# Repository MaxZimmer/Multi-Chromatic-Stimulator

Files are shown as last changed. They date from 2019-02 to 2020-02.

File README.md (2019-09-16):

<p align="right">
<h1 align="center">Multi-Chromatic Stimulator</h1></p>
<h4 align="center">An OpenSource LED stimulator for visual and optogenetics stimulation in combination with 2-photon recording</h4>
<p align="center"><h6 align="right">by M.J.Y. Zimmermann, A.M. Chagas, P. Bartel, T. Baden</h6></p>

This project is licensed under the [GNU General Public License v3.0](https://github.com/MaxZimmer/Multi-Chromatic-Stimulator/blob/master/LICENSE)

The study of colour vision with fluorescence microscopy requires precise control over the spectra of visual stimuli.

Here we describe an effective, low-cost, opensource LED stimulator, designed to be used in combination with a 2-photon microscope. The design is built around an open-source development board and off-the-shelf components. It has been conceived to be assembled and used without the need for advanced electronics skills.

[Instruction Manual](https://github.com/MaxZimmer/Multi-Chromatic-Stimulator/tree/master/Manuscript%20and%20Instruction%20Manual)

***

## Repository structure

```
├───3D Designs                                Contains printed parts for the stimulator and optical components
│   ├───Optical Components
|   |   ├───STL renderings                    - Printing files
|   |   └───SCAD files                        - SCAD files to be modified if need be
│   └───Stimulator
|      ├───STL renderings                    - Printing files
|      └───SCAD files                        - SCAD files to be modified if need be
|
├───Arduino Code                              Stimulator Code
|   ├───Stimulator Code                       - Adaptable C+ code for running the stimulator
|   └───LED driver library                     - Library to run the TLC 5947
|
├───Bill of Materials                         List of necessary components and retailer suggestions
|
├───Datasheets                                - Contains all technical sheet for:
|   ├───Optical Components                    - ...LEDs, Filters, Dichroic Mirrors used in the presented example
|   ├───Stimulator                            - ...micro-controller and LED driver
|   └───Spectrometer                          - ...device used for calibration
|
├───Images                                    Image repository
|
├───Instruction Manual                        Detailed manual to assemble and calibrate the stimulator
|   └───Stimulator Calibration                - Contains calibration recordings and the adaptable jupyter notebook script to calibrate the stimulator
|       ├───Arduino Calibration Code          - Sequence used for the calibration
|       ├───Filters                           - Filters and dicroic mirrors spectra
|       ├───Powermeter Recording              - Recording of the calibration sequence
|       └───Spectrometer Recording            - Recording of the calibration sequence
|
├───PCB                                       KiCad and Gerber files to modified and generate PCB for:
│   ├───Potentiometer mounts                  - ...trimmer potentiometers that set the LED maximum brightness
│   └───Stimulator                            - ...the stimulator itself
|
└───References                                Publication used to design and conceive this model

```

***

The following design can control up to 24 spectral channels with 12 bits linear resolution and 25 μs temporal precision. Our system only requires simple electronics components to be assemble and can be combined.
Built around an ESP32 micro-controller an LED driver (Adafruit model) and off-the-shelf components for a total cost of ~$50

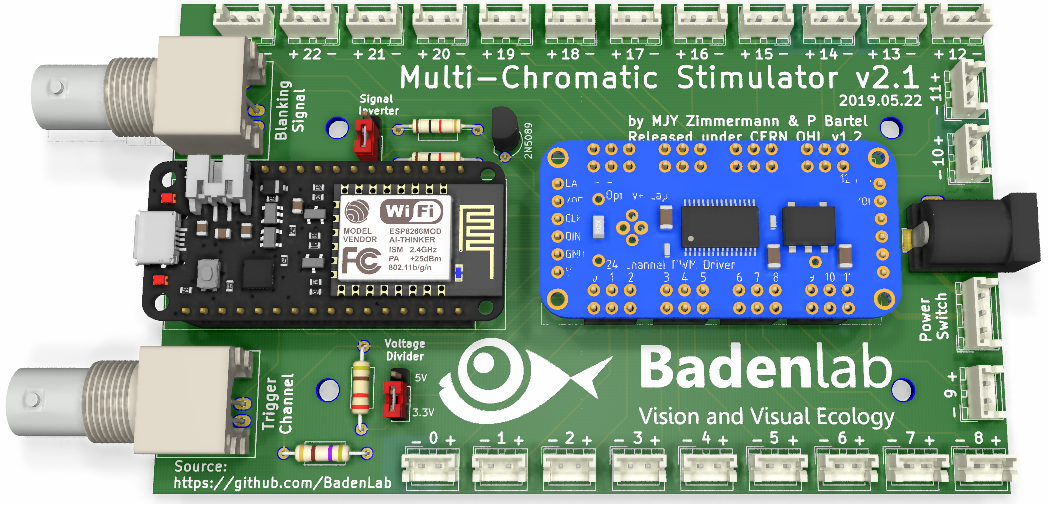
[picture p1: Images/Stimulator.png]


***

The stimulator runs synchronous to the recording system using TTL triggers.
TTL signals correspond to scanning mirror retrace periods and are used to turn ON and OFF LEDs, thus avoiding swamping the PMTs by stimulation light.

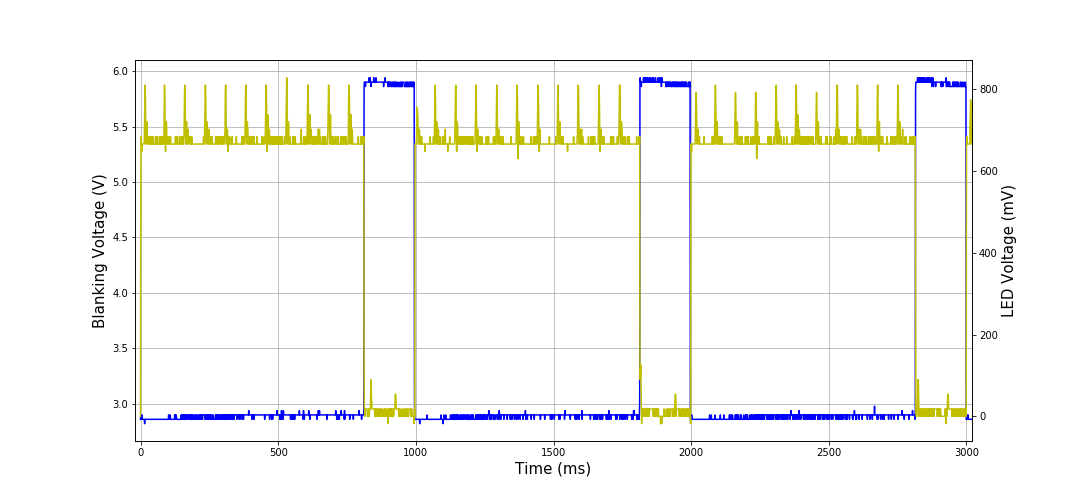
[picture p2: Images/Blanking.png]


***

The following design was adjusted for the tetrachromatic zebrafish.
Stimulating LEDs and optical filters were chosen to match the peak sensitivities of opsin spectra while avoiding overlap with the PMT detection bands.

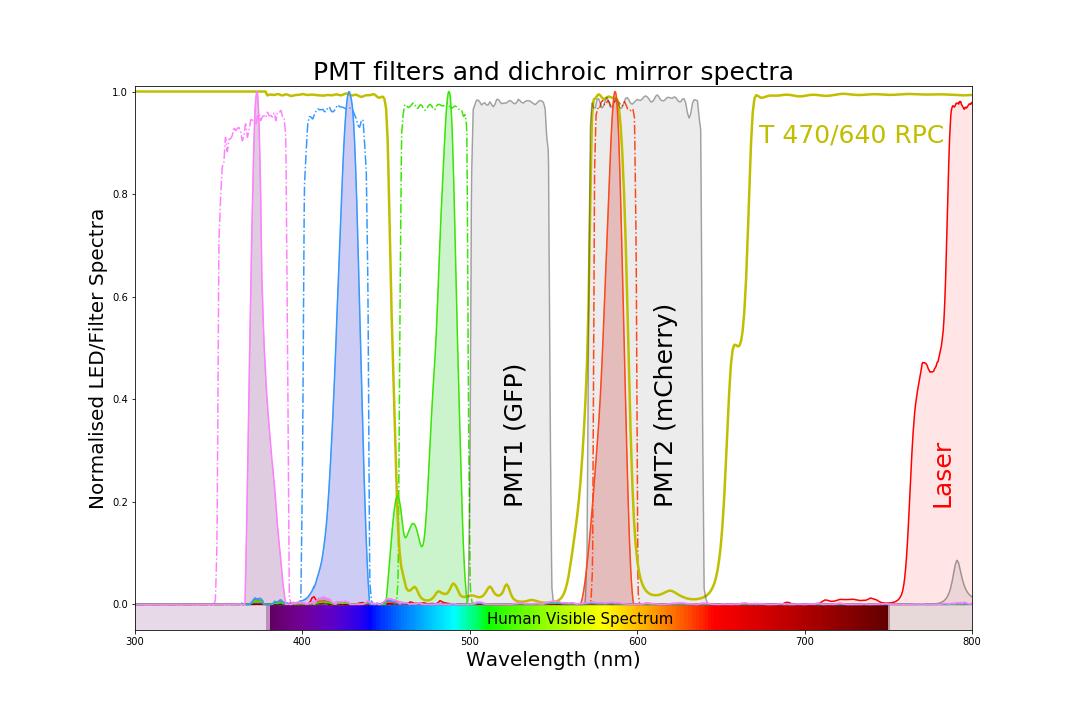
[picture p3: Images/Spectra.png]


***

In this example, light sources are combined and directed through the onjective.

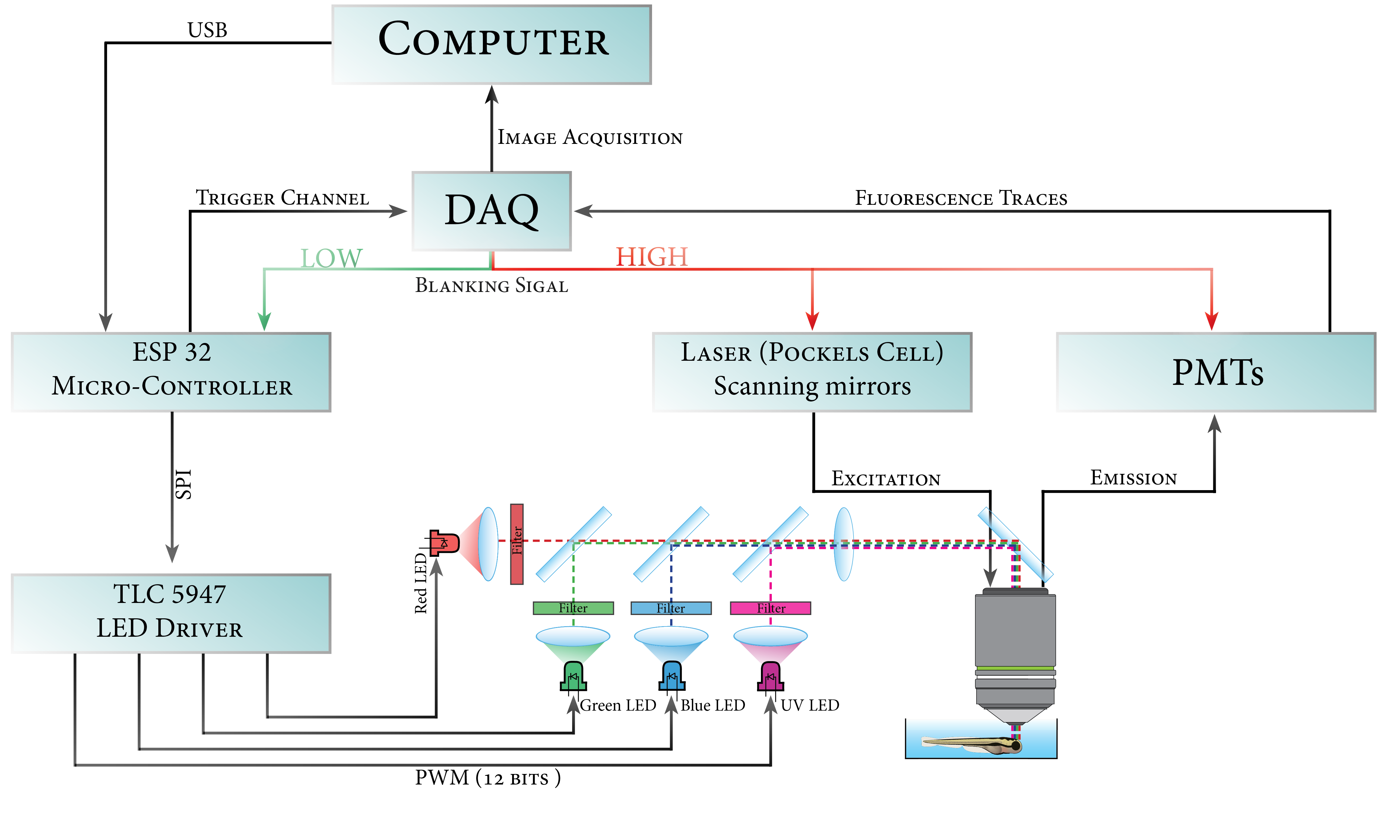
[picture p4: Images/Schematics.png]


***

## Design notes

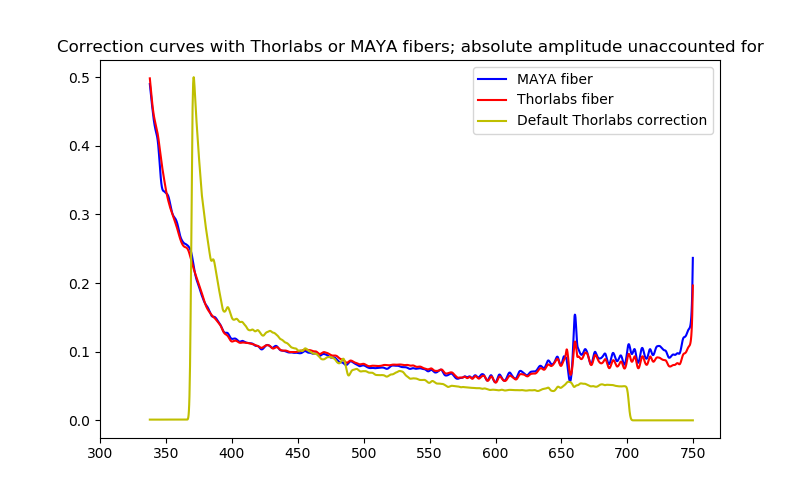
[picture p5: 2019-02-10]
Instruction Manual/Stimulator Calibration/Spectrometer_Recording/Spectrometer Correction Curves/Correction_curves.png

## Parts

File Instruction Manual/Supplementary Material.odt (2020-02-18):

Supplementary Material

Overview

This document contains detailed assembly instructions, a software guideline to customize stimuli, and includes a parts list. The Arduino code and 3D printing files (SCAD and STL) can be downloaded at https://github.com/BadenLab/Tetra-Chromatic-Stimulator/ and further modified to fit customise purposes. The aim of this device is to finely control LEDs used in combination with a 2-photon microscope.

The device consists of a custom-designed PCB, an ESP32 development board (or an Arduino Nano if the stimulator does not need to be combined with a 2-photon microscope), an LED driver and various off-the-shelf components. (Fig. S1).

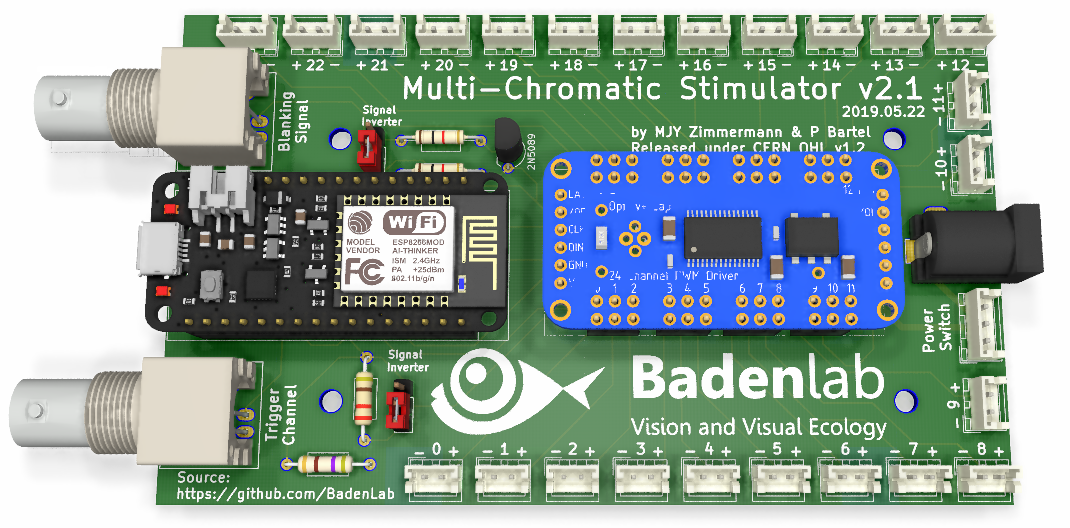
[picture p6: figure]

Figure S1

Bill of Materials

Name | Manufacturer | Order ID | Retailer | Quantity | Observation 1 | Observation 2 | Cost
Adafruit Huzzah32 - ESP32 Feather | Adafruit | 3405 | Adafruit | 1 | Development Board | | £17
Adafruit TLC5947 | Adafruit | 1429 | Adafruit | 1 | LED Driver | | £12
BNC coaxial connectors | TE Connectivity | 1-1337542-0 | Farnell | 2 | Electronics | Right angle jacks, 50ohm | £3.70
2 way JST Female Connector Housing | RS Online | 820-1611 | JST | 8 | Electronics | | £3.80
3 way JST Female Connector Housing | RS Online | 820-1614 | JST | 1 | Electronics | | £1.90
4 way JST Female Connector Housing | RS Online | 820-1618 | JST | 2 | Electronics | | £1.90
2 way JST PCB header | RS Online | 820-1554 | JST | 8 | Electronics | | £3.80
3 way JST PCB header | RS Online | 820-1557 | JST | 1 | Electronics | | £1.90
4 way JST PCB header | RS Online | 820-1551 | JST | 2 | Electronics | | £1.90
JST Crimp Connector Wire | RS Online | 820-1548 | RS | 15 | Electronics | | £10.00
3 mm LED | Digikey | 350-1557-ND | Digikey | 4 | Electronics | 3mm round, Through hole | £2
Mount for 3 mm LED | Digikey | 67-1330-ND | Digikey | 4 | Electronics | 3mm panel mount | £1
Mount for 5 mm LED | Digikey | 67-1332-ND | Digikey | 4 | Electronics | 5mm panel mount | £1
Rocker LED switch | | | Ebay | 1 | Electronics | Round Switch / 3 pins | £2.50
220 Ohms Resistor | RS Online | 707-7612 | RS | 1 | Electronics | Through hole | £1.16
470 Ohms Resistor | RS Online | 707-7647 | RS | 1 | Electronics | Through hole | £1.16
10 kOhms Trimmer Potentiometer | TT Electronics | 89PR10KLF | Farnell | 4 | Electronics | Through Hole | £5.95
PCB socket | Samtec | SSW-116-02-G-S | RS | 6 | Electronics | 1 row, 15 pin | £3
2.1 mm right angle DC socket | RS Online | 884-0957 | RS | 1 | Electronics | 2.1 mm right angle | £1
Solderable Breadboard | Roth Elektronik | RE944-S1 | RS | 1 | Electronics | 42.54 x 31.75 | £1.76
Distinct colour wires | RS Online | 331-862 | RS | 100 cm | Electronics | 20 AWG | £5
Cable shrink | RS Online | 170-6377 | RS | 20 cm | Electronics | Shrunk diameter 1.2 mm | £1.58
M3 x 10mm screw | RS Online | 660-4636 | RS | 4 | Mechanical | M3 x 10 Hex socket cap | £4
M3 nut | RS Online | 122-4400 | RS | 4 | Mechanical | M3 nuts | £4
M4 x 50mm Hex Socket Cap Screws | RS Online | 304-4592 | RS | 4 | Mechanical | M4 x 50 | £4
M4 nut | RS Online | 189-579 | RS | 4 | Mechanical | M4 nuts | £4
| | | | | | | £101

Assembling the Stimulator

1 – Obtaining the custom-designed PCB

From the GitHub repository (https://github.com/BadenLab/Tetra-Chromatic-Stimulator/tree/master/PCB/Stimulator), one can find the gerber.zip folder needed to order the PCB to any manufacturer company (i.e. https://jlcpcb.com). Ordering a minimum of five units should not cost more than £10. Gerber files were designed with KiCad 5.0. Schematics and PCB footprint can be downloaded and modified from the same repository if need be (Fig. S2).

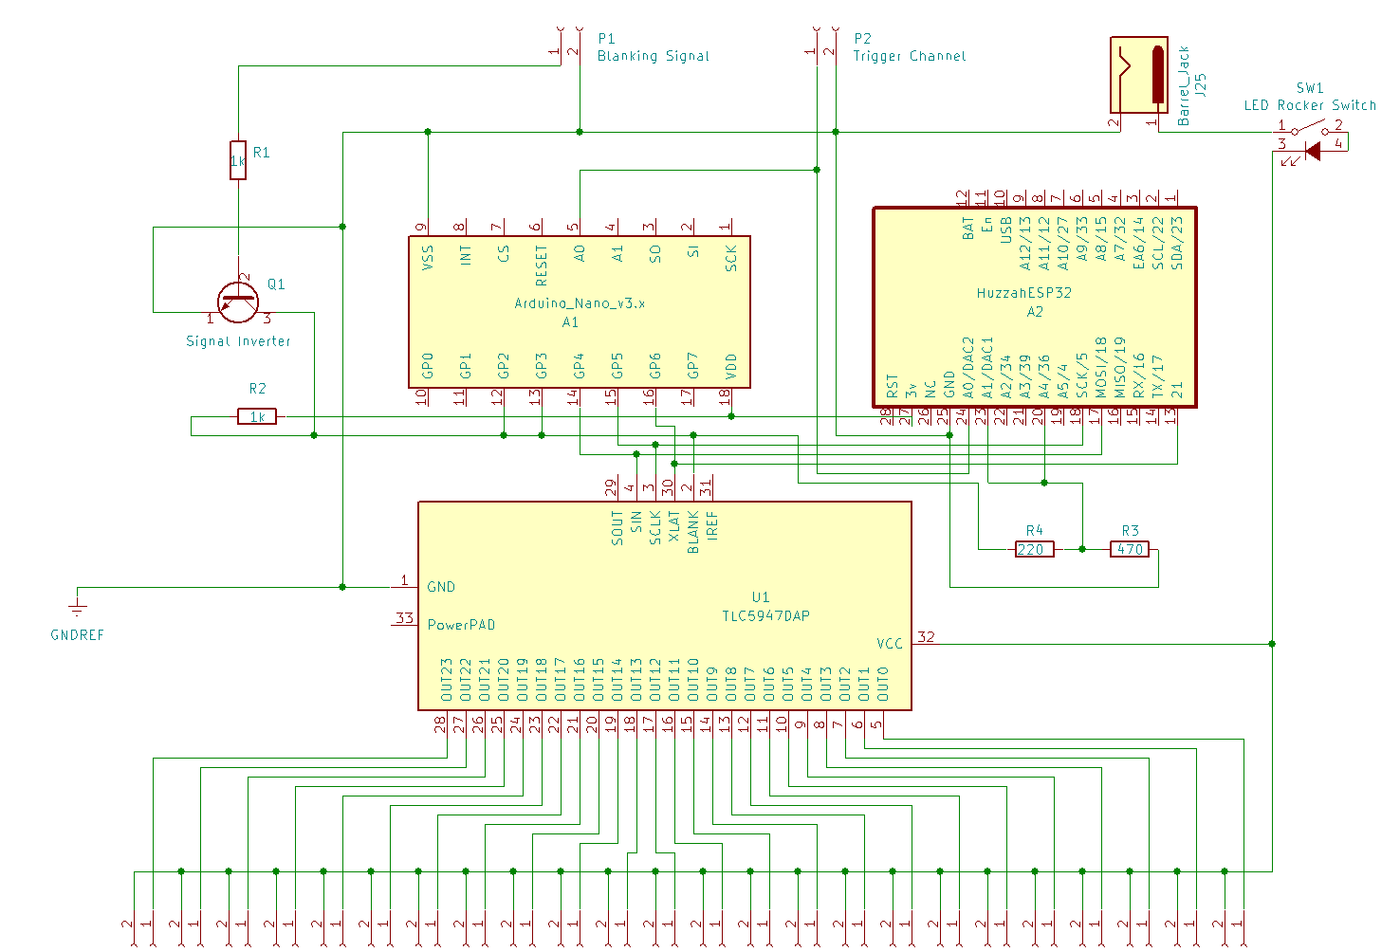
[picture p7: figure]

Supplementary Figure S2.

2 – Soldering the custom-designed PCB

The board is self-explanatory. On the left, two options are available, one for the Arduino (close rows) the other for the ESP (spread rows). There is no need to solder more JST pins that the number of LED required for the desired stimulator (here 8 JST pin are connected: 4 for the stimuli LEDs, 4 for their proxy LEDs).

The jumper on the top (Signal Inverter) allows the inversion of the TTL "Blanking" signals. For ScanImage users, the jumper should be placed at the upper position.

The jumper at the bottom of the board (Voltage Divider) allows to tune down the voltage from 5 to 3.3V if the ESP is used instead of an Arduino. ESP32 unlike Arduino Nano, works on a 3.3V logic; no higher tension should be sent to this board. Since most TTL deliver 5V pulses, we selected a 220/470Ω divider to bring a 5V blanking signal into a 3.3V input. Depending on the blanking signal generator used, this divider can be modified to fit one’s personal design or bypassed by only bridging the 220Ω resistor.

The Adafruit TLC5947 LED driver is a constant current driver configured by default to set the current level at 15mA per channel, which is virtually safe for any LED. However, one can operate at different current by replacing the on-board reference resistor with a through hole resistor. The driver is capable to deliver up to 30mA, the graph in FIG S4 shows the relationship between resistance and output current.

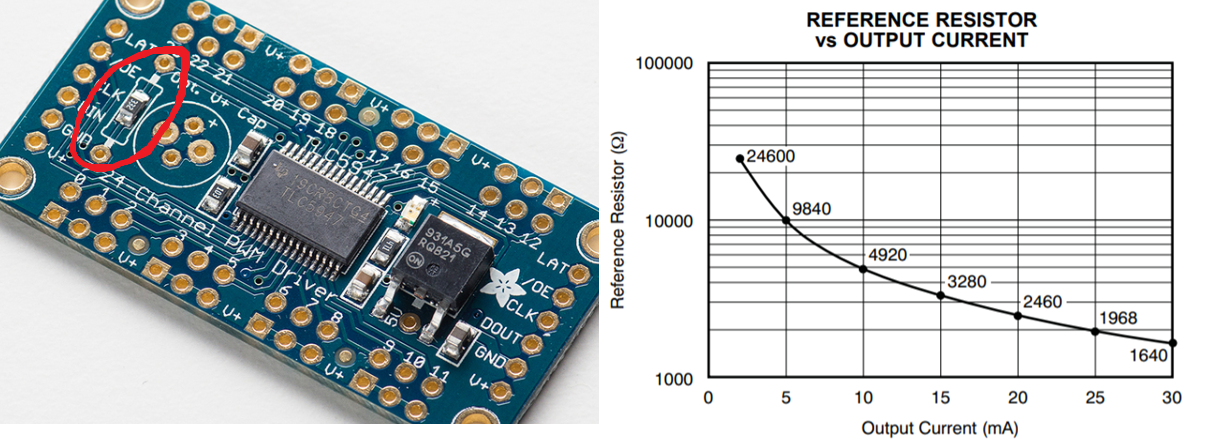
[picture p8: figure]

Supplementary Figure S4

3 – Mounting the potentiometer

In order to finely adjust each LED power, we added multiple-turn trimmer potentiometers to our design. A simple solution is to manufacture the appropriate PCB board (We provide multiple options on the GitHub repository).

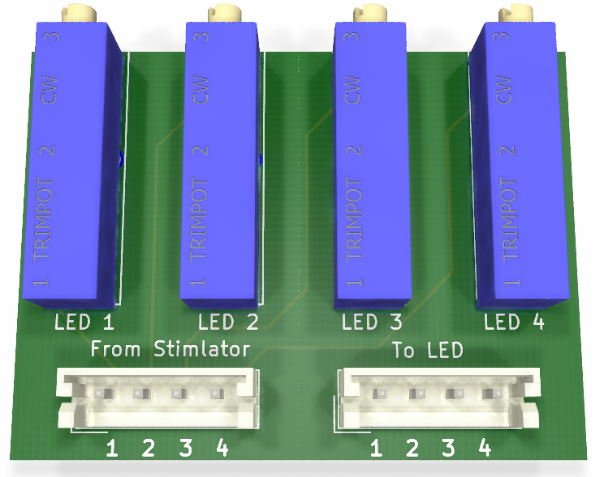
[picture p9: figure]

Otherwise, one can make its own little PCB by using a solderable board. Each potentiometer connects its ClockWise (pin 3) to the LED (+) stimulator JST pin; and its Base (pin 2) to the LED (+) leg. The LED (-) stimulator JST pin connects the LED (-) leg directly.

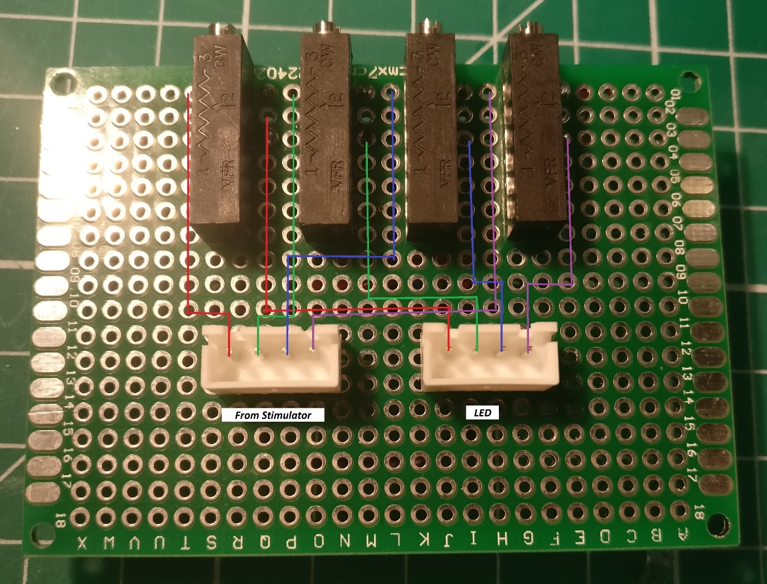
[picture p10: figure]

4 – Printing the Stimulator box

STL files can be found on the GitHub repository and print directly if the user wishes to go for the default design (4 stimulation LEDs + 4 proxy LEDs) and BoM. However, SCAD files are also available and easily adjustable for personalised design (Fig. S6).

We used OpenSCAD (freely available at www.openscad.com) to design the stimulator box. The tolerance of the printer can be adjusted in the “USER Parameters” section of the script (tol =0.1; by default, this value is used for Prusa MK3 and Ultimaker 2). Each component can be displayed/design individually in the “Switches” section. Variables such as LED number (4 by default) and the potentiometer board dimensions can be adjusted in the “Component Parameters” section.

The PCB is screwed to the “Bottom” part of the box by using M3 screws and nuts. The potentiometer board adjusts itself with the “Back” part of the box, and the trimmers should adapt to their respective holes exactly.

All part should fit tightly together and are maintained together by 4 M3*50mm socket screws.

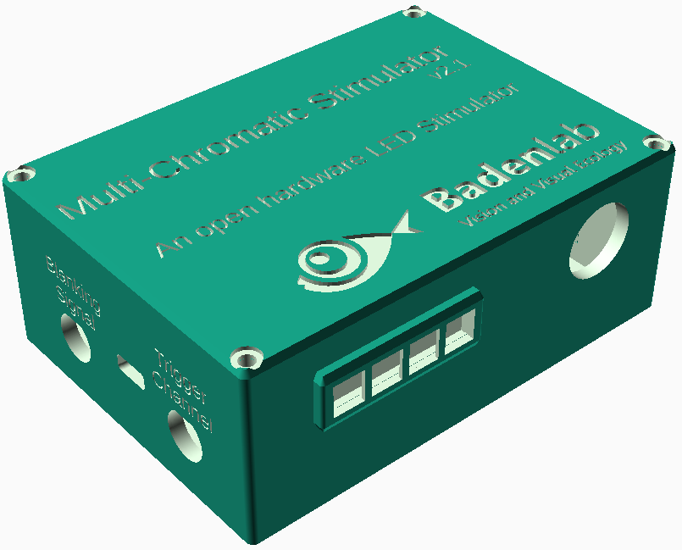
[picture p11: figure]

5 – Adjusting the proxy LED

The proxy LED are markers for the experimenters to have a ready visualisation of the stimulus being displayed under the objective. If this option is selected, 3mm LED are to be mounted at the back of the LED holder using 3mm LED mount. Finally, any translucid material could be placed in the LED holder slot in order to diffuse the proxy LED light (In our example, we used a piece of thin Teflon)

6 – Connecting the Stimulator

The stimulator can be powered from 5 to 30v. The Adafruit TLC5947 being a constant current LED driver, the voltage selection is not critical, however it has to be slightly higher than the LED forward voltage (LED datasheet). Multiple LEDs can be connected to the same channel; however, the voltage supply has to be adjusted in consequence. For example, if an LED has 3.2v forward voltage, then a power supply => 3.2v will be enough, however if 5 of those LEDs are connected in series to the same channel, then the power supply has to be => 3.2v * 5 => 16v.

Blanking signal BNC has to be connected to a TTL (pulse generator), that delivers 5V pulses (if voltage is different, refer yourself to the soldering paragraph). Here we called blanking signal the pulse synchronised with the scanning mirror, the laser pocket cell and the PMTs. On our setup, when blanking signal is HIGH, the scanning mirror starts a new scanning line, the pocket cell let the laser beam through, the PMT records the emitting fluorescence and the stimulating LEDs are turned off. When the blanking signal is LOW, the opposite occurs.

The trigger channel is an output signal generated by the stimulator that by default sends a 3.3v pulse (if ESP32 is used, 5v for Arduino nano) at the start of the stimulus and then at every 1.00000s. This trigger is used during the analysis to correlate the displayed stimulus to the fluorescence trace recordings.

Finally, the board is connected to a computer via micro USB cable (for ESP32, mini USB for Arduino Nano), and ready to be used.

Programming the ESP32 (or Arduino)

1. Download and install Arduino environment on the computer (www.arduino.org).
2. To use the ESP32, a couple of steps are necessary
  a. Install the latest SiLabs CP2104 driver (https://www.silabs.com/products/development-tools/software/usb-to-uart-bridge-vcp-drivers).
  b. Follow the installation instructions from the Espressif repository (https://github.com/espressif/arduino-esp32/blob/master/docs/arduino-ide/boards_manager.md).
3. Install the TLC5947 library
  c. Start Arduino and from the “Sketch” tab, select “Include Library” and open “ Manage Libraries”
  d. From the search bar enter “TLC5947”
  e. Select and Install the library
4. Close Arduino and open the Multi-Chromatic-Stimulator arduino file from the “Arduino Code” folder.
5. From the “Tools” tab:
  f. For the ESP32:
    i. Select from “Boards” the “Adafruit ESP32 Feather”
    ii. From “Upload Speed”, select 921600
    iii. From “Flash Frequency”, select 80Hz
    iv. From “Port”, select the computer port to which the ESP is connected (if doubt, unplug, replug and observe the choices differences). If the ESP is not recognised, check the driver installation (2a.), then check the micro USB cable.
  g. For the Arduino Nano
    v. Select from “Boards” the “Arduino Nano”
    vi. From “Processor”, select “ATmega328P” (option Old Bootloader for clones or older arduino versions)
    vii. From “Port”, select the computer port to which the Arduino is connected (if doubt, unplug, replug and observe the choices differences). If an Arduino clone is used, check that the proper driver is installed on the computer (Board datasheet) then check the mini USB cable.
6. Compile and Upload the code by clicking on the arrow button on the top left.
7. The stimulator is ready to be used.

Operating the Stimulator

The code is organised in five distinct part:

Stimulus Parameters

Here, the user determines the sequence of his looping stimulus.

- The array_LED# corresponds to the sequence of each LED#. The value corresponds to the LED power and CAN ONLY TAKE A VALUE FROM 0 TO 100, where 0 corresponds to no light and 100 to max light intensity
- The array_Time corresponds to the duration of each entry in ms; the first entry being the pre-adaptation that will only be played at the start of the stimulus, the sequence will then loop starting at the second position.
- The number of Loops is determined by nLoops. The stimulus will stop after finishing the n Loop.
- IMPORTANT, for the code to work flawlessly, the number of entries within the arrays has to be the same and manually entered in nArrayEntries (including the pre-adaptation at position 1).

Microcontroller Board Selection

This is where the user defines if he is using an ESP32 or an Arduino Nano

Internal Definitions

This is the main definition part of the code which can be modified to:

- Add more LEDs than the 4 main and 4 proxy defined by default. (Global variables, the LED pins correspond to the pin number on the TLC5947).
- Adjust the trigger duration (25ms by default).
- Adjust the Trigger interval (1000 ms by default)

Internal Methods

This is the main core of the code and should not be structurally changed apart from adding more LEDs (straight forward)

Main Loop

This is where the stimuli controls are defined. By default, when compile window is open (magnifying glass on the top right corner) and the baud rate at the bottom right of the window has be changed to 115200, a manual command will trigger a stimulus:

By default:

- a – Play stimulus at max power
- b – Play stimulus at min power
- 0 – Turn off all LEDs stop any stimulus being played and reset the loop
- + – Turn on all LED to max power
- - – Turn on all LED to min power
- 1 – Turn First LED to max power
- 2 – Turn First LED to min power
- 3 – Turn Second LED to min power
- 4 – Turn Second LED to min power
- 5 – Turn Third LED to min power
- 6 – Turn Third LED to min power
- 7 – Turn Fourth LED to min power
- 8 – Turn Fourth LED to min power

Important to note, obviously the stimulation will only be played if a blanking signal is sent to the board.

Calibrating the stimulator

The TLC5947 is 12 bits PWM grayscale driver, meaning that it offers a 4096 degree of freedom to adjust each LED power.

On the arduino code there is a second tab called “LED_values” which hard-codes the maximum power an LED can get. Those values range from 0 (no current) to 4095 (max current, 15mA by default).

On the default script we proposed two distinct max values (oddly named here max and min power) that can be called individually. The purpose here is to have the opportunity to use the same stimulus sequence at two different light intensities. Off course more can be added manually by the user.

For the calibration, we suggest setting the max_LED# value at 4095 (Full power) and use successively a spectrometer and a powermeter. To adjust the LED brightness, the user should first use the trimmer potentiometer at the back of the stimulator then finely tune the desired max power in the code. When the LED value (0-100) will be entered in the stimulus sequence, it will automatically be mapped to 0-max_LED#

In this document we will used, as example, the visual stimulator built for the chromatic visual study of one of our animal models: the larval zebrafish. As this model possesses four cones photoreceptors that can be categorized as Red-, Green-, Blue- and UV-sensitive we designed a custom-built tetrachromatic stimulator with four LEDs that matches the peak sensitivity of those photoreceptors.

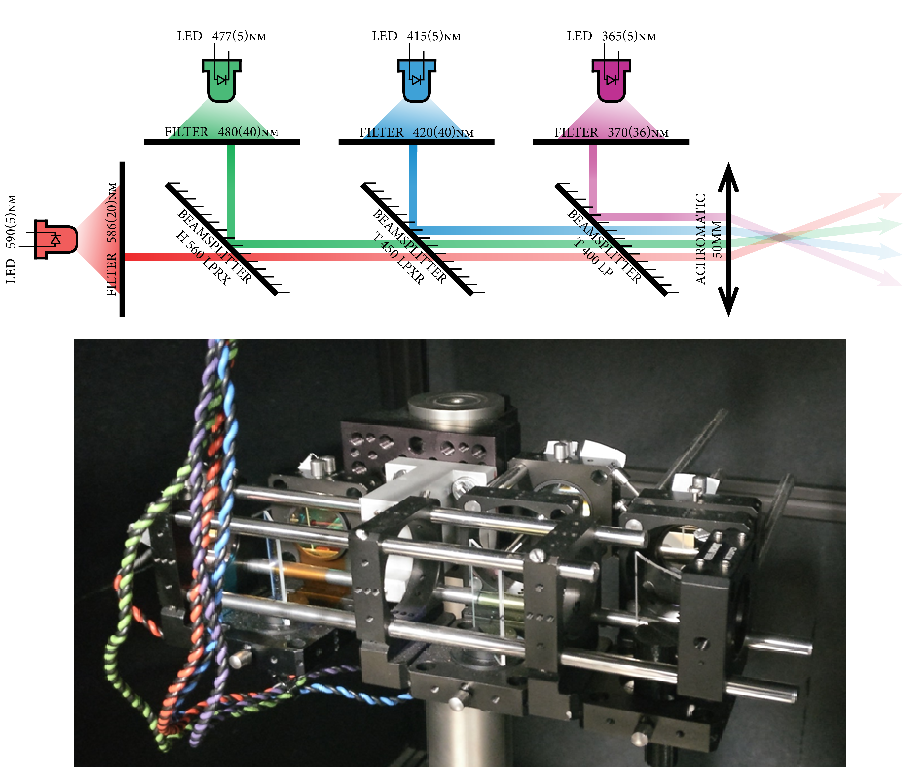
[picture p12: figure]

Optogenetics Stimulator

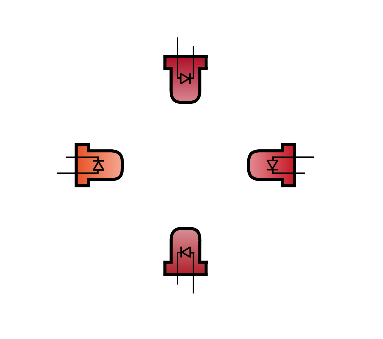
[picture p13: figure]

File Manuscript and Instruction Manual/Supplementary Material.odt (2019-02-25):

Supplementary Material

MultiChromatic Stimulator (need a proper name): an opensource LED stimulator for visual and optogenetics stimulation in combination with 2-photon recording

M.J.Y. Zimmermann, A.M. Chagas, P. Bartel, T. Baden

Affiliations:

1. School of Life Sciences, University of Sussex, United Kingdom
2. Institute for Ophthalmic Research, University of Tuebingen, Germany
3. TReND in Africa gUG (www.TReNDinAfrica.org)

Correspondence: T.B.: t.baden@sussex.ac.uk

Need illustration picture

Name | Manufacturer | Order ID | Retailer | Quantity | Observation 1 | Observation 2 | Cost
Adafruit Huzzah32 - ESP32 Feather | Adafruit | 3405 | Adafruit | 1 | Development Board | Easier to order it with header pins soldered | £17
Adafruit TLC5947 | Adafruit | 1429 | Adafruit | 1 | LED Driver | | £12
BNC coaxial connectors | TE Connectivity | 1-1337542-0 | Farnell | 2 | Electronics | Right angle jacks, 50ohm | £3.70
2 way JST Female Connector Housing | RS Online | 820-1611 | JST | 8 | Electronics | | £3.80
3 way JST Female Connector Housing | RS Online | 820-1614 | JST | 1 | Electronics | | £1.90
4 way JST Female Connector Housing | RS Online | 820-1618 | JST | 2 | Electronics | | £1.90
2 way JST PCB header | RS Online | 820-1554 | JST | 8 | Electronics | | £3.80
3 way JST PCB header | RS Online | 820-1557 | JST | 1 | Electronics | | £1.90
4 way JST PCB header | RS Online | 820-1551 | JST | 2 | Electronics | | £1.90
JST Crimp Connector Wire | RS Online | 01SHXSXH-26L 150 | RS | 15 | Electronics | | £10.00
3 mm LED | Digikey | 350-1557-ND | Digikey | 4 | Electronics | 3mm round, tht | £2
Mount for 3 mm LED | Digikey | 67-1330-ND | Digikey | 4 | Electronics | 3mm panel mount | £1
Mount for 5 mm LED | Digikey | 67-1332-ND | Digikey | 4 | Electronics | 5mm panel mount | £1
Rocker LED switch | | | Ebay | 1 | Electronics | Round Switch / 3 pins | £2.50
220 Ohms Resistor | RS Online | 707-7612 | RS | 1 | Electronics | Through hole | £1.16
470 Ohms Resistor | RS Online | 707-7647 | RS | 1 | Electronics | Through hole | £1.16
10 kOhms Trimmer Potentiometer | TT Electronics | 89PR10KLF | Farnell | 4 | Electronics | Through Hole | £5.95
PCB socket | Samtec | SSW-116-02-G-S | RS | 6 | Electronics | 1 row, 15 pin | £3
2.1 mm right angle DC socket | RS Online | 884-0957 | RS | 1 | Electronics | 2.1 mm right angle | £1
Solderable Breadboard | Roth Elektronik | RE944-S1 | RS | 1 | Electronics | 42.54 x 31.75 | £1.76
distinc colour wires | RS Online | 331-862 | RS | 100 cm | Electronics | 20 AWG | £5
Cable shrink | RS Online | 170-6377 | RS | 20 cm | Electronics | Shrunk diameter 1.2 mm | £1.58
M3 x 10mm screw | RS Online | 660-4636 | RS | 4 | Mechanical | M3 x 10 Hex socket cap | £4
M3 nut | RS Online | 122-4400 | RS | 4 | Mechanical | M3 nuts | £4
M4 x 50mm Hex Socket Cap Screws | RS Online | 304-4592 | RS | 4 | Mechanical | M4 x 50 | £4
M4 nut | RS Online | 189-579 | RS | 4 | Mechanical | M4 nuts | £4
| | | | | | | £101

Overview

This document contains detailed assembly instructions, a software guideline to customize stimuli, and includes a parts list. The Arduino code and 3D printing files (SCAD and STL) can be downloaded at https://github.com/BadenLab/Stimulator????, and further modified to fit customise purposes. The aim of this device is to finely control LEDs used in combination with a 2-photon microscope.

The device consists of a custom-designed PCB, a ESP32 development board (or an Arduino Nano if the stimulator does not need to be combined with a 2 photon microscope), a LED driver and various off-the-shelf components. (Fig. S1).


Supplementary Figure S1

Assembling the Stimulator

1 – Obtaining the custom-designed PCB

From the GitHub repository (https://github.com/BadenLab/?????/PCB), one can find the gerber.zip folder needed to order the PCB to any manufacturer company (i.e. https://jlcpcb.com). Ordering a minimum of 5 units should not cost more than £10. Gerber files were designed with KiCad 5.0. Schematics and PCB footprint can be downloaded and modified from the same repository if need be (Fig. S2).


Supplementary Figure S2.

2 – Soldering the custom-designed PCB

The board is self-explanatory (Fig. S3). On the left, two options are available, one for the Arduino (close rows) the other for the ESP (spread rows). There is no need to solder more JST pins that the number of LED required for the desired stimulator (here 8 JST pin are connected: 4 for the stimuli LEDs, 4 for their proxy LEDs). The two resistors at the bottom are a voltage divider for the ESP32 only (There’s no need to solder any resistor here if the Arduino option is chosen). ESP32 unlike Arduino Nano, works on a 3.3V logic; no higher tension should be sent to this board. Since most TTL deliver 5V pulses, we selected a 220/470Ω divider to bring a 5V blanking signal into a 3.3V input. Depending on the blanking signal generator used, this divider can be modified to fit one’s personal design or bypassed by only bridging the 220Ω resistor.

Supplementary Figure S3 TESSA PICTURE

The Adafruit TLC5947 LED driver is a constant current driver configured by default to set the current level at 15mA per channel, which is virtually safe for any LED. However, one can operate at different current by replacing the on-board reference resistor with a through hole resistor. The driver is capable to deliver up to 30mA, the graph in FIG S4 shows the relationship between resistance and output current.


Supplementary Figure S4

3 – Mounting the potentiometer

In order to finely adjust each LED power, we added multiple-turn trimmer potentiometers to our design. A simple solution is to manufacture the appropriate PCB board (We provide multiple option on the GitHub repository). Otherwise, one can make its own little PCB by using a solderable board and connect the potentiometer as shown on FIG S5.

Each potentiometer connects its ClockWise (pin 3) to the LED (+) stimulator JST pin; and its Base (pin 2) to the LED (+) leg. The LED (-) stimulator JST pin connects the LED (-) leg directly.


Supplementary Figure S5

4 – Printing the Stimulator box

STL files can be found on the GitHub repository and print directly if the user wishes to go for the default design (4 stimulation LEDs + 4 proxy LEDs) and BoM. However, SCAD files are also available and easily adjustable for personalised design (Fig. S6).

We used OpenSCAD (freely available at www.openscad.com) to design the stimulator box. The tolerance of the printer can be adjusted in the “USER Parameters” section of the script (tol =0.1; by default, this value is used for Prusa MK3 and Ultimaker 2). Each component can be displayed/design individually in the “Switches” section. Variables such as LED number (4 by default) and the potentiometer board dimensions can be adjusted in the “Component Parameters” section.

The PCB is screwed to the “Bottom” part of the box by using M3 screws and nuts. The potentiometer board adjusts itself with the “Back” part of the box, and the trimmers should adapt to their respective holes exactly.

All part should fit tightly together and are maintained together by 4 M3*50mm socket screws.


Supplementary Figure S6

5 – Adjusting the proxy LED

The proxy LED are markers for the experimenters to have a ready visualisation of the stimulus being displayed under the objective. If this option is selected, 3mm LED are to be mounted at the back of the LED holder using 3mm LED mount (Fig S7). Finally, any translucid material could be placed in the LED holder slot in order to diffuse the proxy LED light (In our example, we used a piece of thin Teflon)

TESSA PICTURE OF THE LED HOLDER Supplementary Figure S7

6 – Connecting the Stimulator

The stimulator can be powered from 5 to 30v. The Adafruit TLC5947 being a constant current LED driver, the voltage selection is not critical, however it has to be slightly higher than the LED forward voltage (LED datasheet). Multiple LEDs can be connected to the same channel; however, the voltage supply has to be adjusted in consequence. For example, if an LED has 3.2v forward voltage, then a power supply => 3.2v will be enough, however if 5 of those LEDs are connected in series to the same channel, then the power supply has to be => 3.2v * 5 => 16v.

Blanking signal BNC has to be connected to a TTL (pulse generator), that delivers 5V pulses (if voltage is different, refer yourself to the soldering paragraph). Here we called blanking signal the pulse synchronised with the scanning mirror, the laser pocket cell and the PMTs. On our setup, when blanking signal is HIGH, the scanning mirror starts a new scanning line, the pocket cell let the laser beam through, the PMT records the emitting fluorescence and the stimulating LEDs are turned off. When the blanking signal is LOW, the opposite occurs.

The trigger channel is an output signal generated by the stimulator that by default sends a 3.3v pulse (if ESP32 is used, 5v for Arduino nano) at the start of the stimulus and then at every 1.00000s. This trigger is used during the analysis to correlate the displayed stimulus to the fluorescence trace recordings.

Finally, the board is connected to a computer via micro USB cable (for ESP32, mini USB for Arduino Nano), and ready to be used.

Programming the ESP32 (or Arduino)

1. Download and install Arduino environment on the computer (www.arduino.org).
2. To use the ESP32, a couple of steps are necessary
  a. Install the latest SiLabs CP2104 driver (https://www.silabs.com/products/development-tools/software/usb-to-uart-bridge-vcp-drivers).
  b. Follow the installation instructions from the Espressif repository (https://github.com/espressif/arduino-esp32/blob/master/docs/arduino-ide/boards_manager.md).
3. Install the TLC5947 library
  c. Start Arduino and from the “Sketch” tab, select “Include Library” and open “ Manage Libraries”
  d. From the search bar enter “TLC5947”
  e. Select and Install the library
4. Close Arduino and open the Multi-Chromatic-Stimulator arduino file from the “Arduino Code” folder.
5. From the “Tools” tab:
  f. For the ESP32:
    i. Select from “Boards” the “Adafruit ESP32 Feather”
    ii. From “Upload Speed”, select 921600
    iii. From “Flash Frequency”, select 80Hz
    iv. From “Port”, select the computer port to which the ESP is connected (if doubt, unplug, replug and observe the choices differences). If the ESP is not recognised, check the driver installation (2a.), then check the micro USB cable.
  g. For the Arduino Nano
    v. Select from “Boards” the “Arduino Nano”
    vi. From “Processor”, select “ATmega328P” (option Old Bootloader for clones or older arduino versions)
    vii. From “Port”, select the computer port to which the Arduino is connected (if doubt, unplug, replug and observe the choices differences). If an Arduino clone is used, check that the proper driver is installed on the computer (Board datasheet) then check the mini USB cable.
6. Compile and Upload the code by clicking on the arrow button on the top left.
7. The stimulator is ready to be used.

Operating the Stimulator

The code is organised in five distinct part:

Stimulus Parameters

Here, the user determines the sequence of his looping stimulus.

- The array_LED# corresponds to the sequence of each LED#. The value corresponds to the LED power and CAN ONLY TAKE A VALUE FROM 0 TO 100, where 0 corresponds to no light and 100 to max light intensity
- The array_Time corresponds to the duration of each entry in ms; the first entry being the pre-adaptation that will only be played at the start of the stimulus, the sequence will then loop starting at the second position.
- The number of Loops is determined by nLoops. The stimulus will stop after finishing the n Loop.
- IMPORTANT, for the code to work flawlessly, the number of entries within the arrays has to be the same and manually entered in nArrayEntries (including the pre-adaptation at position 1).

Microcontroller Board Selection

This is where the user defines if he is using an ESP32 or an Arduino Nano

Internal Definitions

This is the main definition part of the code which can be modified to:

- Add more LEDs than the 4 main and 4 proxy defined by default. (Global variables, the LED pins correspond to the pin number on the TLC5947).
- Adjust the trigger duration (25ms by default).
- Adjust the Trigger interval (1000 ms by default)

Internal Methods

This is the main core of the code and should not be structurally changed apart from adding more LEDs (straight forward)

Main Loop

This is where the stimuli controls are defined. By default, when compile window is open (magnifying glass on the top right corner) and the baud rate at the bottom right of the window has be changed to 115200, a manual command will trigger a stimulus:

By default:

- a – Play stimulus at max power
- b – Play stimulus at min power
- 0 – Turn off all LEDs stop any stimulus being played and reset the loop
- + – Turn on all LED to max power
- - – Turn on all LED to min power
- 1 – Turn First LED to max power
- 2 – Turn First LED to min power
- 3 – Turn Second LED to min power
- 4 – Turn Second LED to min power
- 5 – Turn Third LED to min power
- 6 – Turn Third LED to min power
- 7 – Turn Fourth LED to min power
- 8 – Turn Fourth LED to min power

Important to note, obviously the stimulation will only be played if a blanking signal is sent to the board.

Calibrating the stimulator

The TLC5947 is 12 bits PWM grayscale driver, meaning that it offers a 4096 degree of freedom to adjust each LED power.

On the arduino code there is a second tab called “LED_values” which hard-codes the maximum power an LED can get. Those values range from 0 (no current) to 4095 (max current, 15mA by default).

On the default script we proposed 2 distinct max values (oddly named here max and min power) that can be called individually. The purpose here is to have the opportunity to use the same stimulus sequence at two different light intensities. Off course more can be added manually by the user.

For the calibration, we suggest setting the max_LED# value at 4095 (Full power) and use successively a spectrometer and a powermeter. To adjust the LED brightness, the user should first use the trimmer potentiometer at the back of the stimulator then finely tune the desired max power in the code. When the LED value (0-100) will be entered in the stimulus sequence, it will automatically be mapped to 0-max_LED#

In this document we will used, as example, the visual stimulator built for the chromatic visual study of one of our animal models: the larval zebrafish. As this model possesses four cones photoreceptors that can be categorized as Red-, Green-, Blue- and UV-sensitive we designed a custom-built tetrachromatic stimulator with four LEDs that matches the peak sensitivity of those photoreceptors.


Optogenetics Stimulator


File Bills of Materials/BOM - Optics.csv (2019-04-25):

Name | Part id | Manufacturer | order id | Retailer | Quantity | obs1 | obs2 | obs3 | URL
Red LED | B5B-434-TY | Roithner |  | Roitner | 1 | LED |  | 5mm | http://www.roithner-laser.com/led_diverse.html
Green LED | RLS-5B475-S | Roithner |  | Roitner | 1 | LED |  | 5mm | http://www.roithner-laser.com/led_diverse.html
Blue LED | VL415-5-15 | Roithner |  | Roitner | 1 | LED |  | 5mm | http://www.roithner-laser.com/led_diverse.html
UV LED | XSL-365-5E | Roithner |  | Roitner | 1 | LED |  | 5mm | http://www.roithner-laser.com/led_diverse.html
Red LED Filter | FF01-586/20 BrightLine HC | Semrock | F39-587 | AHF | 1 | Band Pass Filter |  | 22.9mm | https://www.ahf.de/en/products/spectral-analysis-photonic/optical-filters/individual-filters/bandpass-filters/500-599-nm/2098/586/20-brightline-hc?c=499
Green LED Filter | ET 480/40 | Chroma | F49-480 | AHF | 1 | Band Pass Filter |  | 22.9mm | https://www.ahf.de/en/products/spectral-analysis-photonic/optical-filters/individual-filters/bandpass-filters/400-499-nm/2598/480/40x-et-bandpass
Blue LED Filter | ET 420/40 | Chroma | F47-420 | AHF | 1 | Band Pass Filter |  | 22.9mm | https://www.ahf.de/en/products/spectral-analysis-photonic/optical-filters/individual-filters/bandpass-filters/400-499-nm/2370/420/40-et-bandpass
UV LED Filter | FF01-370/36 BrightLine HC | Semrock | F39-370 | AHF | 1 | Band Pass Filter |  | 22.9mm | https://www.ahf.de/en/products/spectral-analysis-photonic/optical-filters/individual-filters/bandpass-filters/200-399-nm/1985/370/36-brightline-hc
U/RGB Beamsplitter | T 400 LP | Chroma | F79-100 | AHF | 1 | Dichroic Mirror |  | 25.5X36X1mm | https://www.ahf.de/en/products/spectral-analysis-photonic/optical-filters/dichroic-beamsplitters/beamsplitters-for-epi-fluorescence/standard-beamsplitters/lon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
B/RG Beamsplitter | T 450l LPXR | Chroma | F48-450 | AHF | 1 | Dichroic Mirror |  | 25.5X36X1mm | https://www.ahf.de/en/products/spectral-analysis-photonic/optical-filters/dichroic-beamsplitters/beamsplitters-for-epi-fluorescence/standard-beamsplitters/lon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
G/R Beamsplitter | H 560 LPXR | AHF | F48-559 | AHF | 1 | Dichroic Mirror |  | 25.5X36X1mm | https://www.ahf.de/en/products/spectral-analysis-photonic/optical-filters/dichroic-beamsplitters/laser-beamsplitters/longpass-laser-beamsplitters/single/2517/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
50mm Lens | ACA254-050-A | ThorLabs | ACA254-050-A | ThorLabs | 1 | 350-750 nm |  | 25.4 * 13.3mm | https://www.thorlabs.com/thorproduct.cfm?partnumber=ACA254-050-A
Cage System Right-Angle Adapter | LCP30 | ThorLabs | LCP30 | ThorLabs | 3 | Cage Assembly |  | 60mm to 30mm | https://www.thorlabs.com/thorproduct.cfm?partnumber=LCP30
Cage Plate Adapter | LCP02/M | ThorLabs | LCP02 | ThorLabs | 2 | Cage Assembly |  | 30mm to 60mm | https://www.thorlabs.com/thorproduct.cfm?partnumber=LCP02/M
Cage Plate | CP02T/M | ThorLabs | CP02T/M | ThorLabs | 4 | Cage Assembly |  | 30mm x 0.5" threaded | https://www.thorlabs.com/thorproduct.cfm?partnumber=CP02T/M
Assembly Rod | ER8 | ThorLabs | ER8-P4 | ThorLabs | 4 | Cage Assembly |  | 6mmx8" | https://www.thorlabs.com/thorproduct.cfm?partnumber=ER8-P4
Assembly Rod | ER6 | ThorLabs | ER6-P4 | ThorLabs | 4 | Cage Assembly |  | 6mmx6" | https://www.thorlabs.com/thorproduct.cfm?partnumber=ER6-P4
Assembly Rod | ER4 | ThorLabs | ER4-P4 | ThorLabs | 4 | Cage Assembly |  | 6mmx4" | https://www.thorlabs.com/thorproduct.cfm?partnumber=ER4-P4
Assembly Rod | ER2 | ThorLabs | ER2-P4 | ThorLabs | 4 | Cage Assembly |  | 6mmx2" | https://www.thorlabs.com/thorproduct.cfm?partnumber=ER2-P4
Assembly Rod | ER1 | ThorLabs | ER1-P4 | ThorLabs | 4 | Cage Assembly |  | 6mmx1" | https://www.thorlabs.com/thorproduct.cfm?partnumber=ER1-P4
Mounting Post | P10 | ThorLabs | P10 | ThorLabs | 1 | Cage Assembly |  | 1/4" x 10" | https://www.thorlabs.com/thorproduct.cfm?partnumber=P10
Base Adapter | PB4 | ThorLabs | PB4 | ThorLabs | 1 | Cage Assembly |  | 1/4" Thread | https://www.thorlabs.com/thorproduct.cfm?partnumber=PB4
Cage Clamp | CH1560/M | ThorLabs | CH1560/M | ThorLabs | 1 | Cage Assembly |  | 1.5" Post | https://www.thorlabs.com/thorproduct.cfm?partnumber=CH1560/M

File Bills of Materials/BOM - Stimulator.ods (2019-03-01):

Name | Manufacturer | Order ID | Retailer | Quantity | Observation 1 | Observation 2 | Suggested URL | Cost
Adafruit Huzzah32 - ESP32 Feather | Adafruit | 3405 | Adafruit | 1 | Development Board | Easier to order it with header pins soldered | https://www.adafruit.com/product/3405 | £17
Adafruit TLC5947 | Adafruit | 1429 | Adafruit | 1 | LED Driver |  | https://www.adafruit.com/product/1429 | £12
BNC coaxial connectors | TE Connectivity | 1-1337542-0 | Farnell | 2 | Electronics | Right angle jacks, 50ohm | https://uk.farnell.com/greenpar-te-connectivity/1-1337542-0/rf-coaxial-bnc-right-angle-jack/dp/1020954?st=bnc%20pcb%20mout | £3.70
2 way JST Female Connector Housing | RS Online | 820-1611 | JST | 8 | Electronics |  | https://uk.rs-online.com/web/p/pcb-connector-housings/8201611/ | £3.80
3 way JST Female Connector Housing | RS Online | 820-1614 | JST | 1 | Electronics |  | https://uk.rs-online.com/web/p/pcb-connector-housings/8201614/ | £1.90
4 way JST Female Connector Housing | RS Online | 820-1618 | JST | 2 | Electronics |  | https://uk.rs-online.com/web/p/pcb-connector-housings/8201618/ | £1.90
2 way JST PCB header | RS Online | 820-1554 | JST | 8 | Electronics |  | https://uk.rs-online.com/web/p/pcb-headers/8201554/ | £3.80
3 way JST PCB header | RS Online | 820-1557 | JST | 1 | Electronics |  | https://uk.rs-online.com/web/p/pcb-headers/8201557/ | £1.90
4 way JST PCB header | RS Online | 820-1551 | JST | 2 | Electronics |  | https://uk.rs-online.com/web/p/pcb-headers/8201551/ | £1.90
JST Crimp Connector Wire | RS Online | 01SHXSXH-26L 150 | RS | 15 | Electronics |  | https://uk.rs-online.com/web/p/products/8201548/ | £10.00
3 mm LED | Digikey | 350-1557-ND | Digikey | 4 | Electronics | 3mm round, tht | https://www.digikey.com/product-detail/en/dialight/5219210F/350-1557-ND/808955 | £2
Mount for 3 mm LED | Digikey | 67-1330-ND | Digikey | 4 | Electronics | 3mm panel mount | https://www.digikey.com/products/en?keywords=67-1330-ND | £1
Mount for 5 mm LED | Digikey | 67-1332-ND | Digikey | 4 | Electronics | 5mm panel mount | https://www.digikey.com/product-detail/en/lumex-opto-components-inc/SSH-LX5091/67-1332-ND/144810 | £1
Rocker LED switch |  |  | Ebay | 1 | Electronics | Round Switch / 3 pins | https://www.ebay.co.uk/p/Blue-On-off-Lighted-LED-Round-Rocker-Switch-Car-Dashboard-Dash-SPST-12v/1942302409?iid=262042885084&chn=ps | £2.50
220 Ohms Resitor | RS Online | 707-7612 | RS | 1 | Electronics | Through hole | https://uk.rs-online.com/web/p/through-hole-fixed-resistors/7077612/ | £1.16
470 Ohms Resitor | RS Online | 707-7647 | RS | 1 | Electronics | Through hole | https://uk.rs-online.com/web/p/through-hole-fixed-resistors/7077647/ | £1.16
10 kOhms Trimmer Potentiometer | TT Electronics | 89PR10KLF | Farnell | 4 | Electronics | Through Hole | https://uk.farnell.com/bi-technologies-tt-electronics/89pr10klf/trimmer-resistor/dp/1653213?st=trimmer%20potentiometer | £5.95
PCB socket | Samtec | SSW-116-02-G-S | RS | 6 | Electronics | 1 row, 15 pin | https://uk.rs-online.com/web/p/pcb-sockets/7655795/ | £3
2.1 mm right angle DC socket | RS Online | 884-0957 | RS | 1 | Electronics | 2.1 mm right angle | https://uk.rs-online.com/web/p/dc-power-sockets/8840957/ | £1
Solderable Breadboard | Roth Elektronik | RE944-S1 | RS | 1 | Electronics | 42.54 x 31.75 | https://uk.rs-online.com/web/p/breadboards/8971654/ | £1.76
distinc colour wires | RS Online | 331-862 | RS | 100 cm | Electronics | 20 AWG | https://uk.rs-online.com/web/p/hookup-equipment-wire/0331862/ | £5
Cable shrink | RS Online | 170-6377 | RS | 20 cm | Electronics | Shrunk diameter 1.2 mm | https://uk.rs-online.com/web/p/heat-shrink-cold-shrink-sleeves/1706377/ | £1.58
M3 x 10mm screw | RS Online | 660-4636 | RS | 4 | Mechanical | M3 x 10 Hex socket cap | https://uk.rs-online.com/web/p/socket-screws/6604636/ | £4
M3 nut | RS Online | 122-4400 | RS | 4 | Mechanical | M3 nuts | https://uk.rs-online.com/web/p/hex-nuts/1224400/ | £4
M4 x 50mm Hex Socket Cap Screws | RS Online | 304-4592 | RS | 4 | Mechanical | M4 x 50 | https://uk.rs-online.com/web/p/socket-screws/3044592/ | £4
M4 nut | RS Online | 189-579 | RS | 4 | Mechanical | M4 nuts | https://uk.rs-online.com/web/p/hex-nuts/0189579/ | £4
 |  |  |  |  |  |  |  | £101

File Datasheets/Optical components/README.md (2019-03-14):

<p align="right">

This project is licensed under the [GNU General Public License v3.0](https://github.com/MaxZimmer/Multi-Chromatic-Stimulator/blob/master/LICENSE)

***



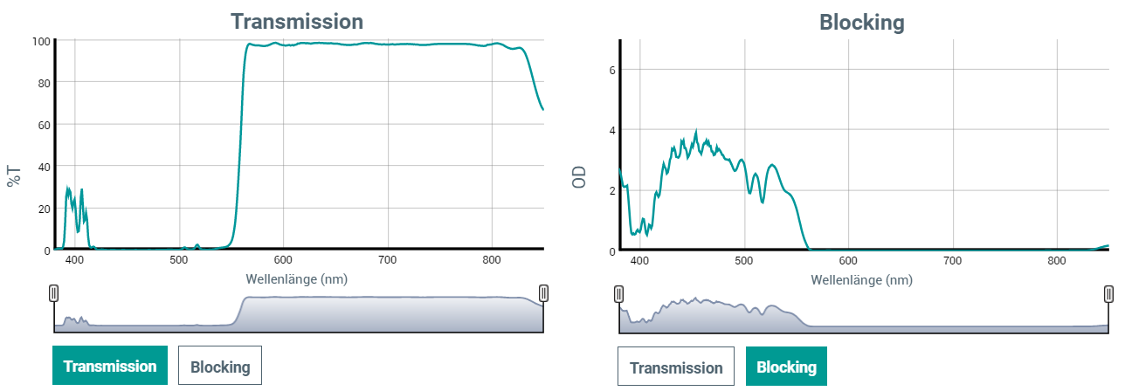
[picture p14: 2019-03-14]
Datasheets/Optical components/Dichroic Mirrors/T 560 LPXR/T 560 LPXR.png

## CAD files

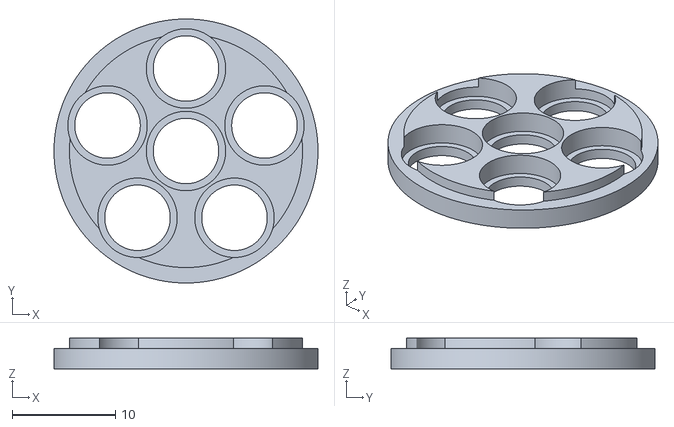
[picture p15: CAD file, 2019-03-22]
3D Designs/Optical Components/STL Files/6_LED_Holder.stl
25.6 x 25.6 x 3.00

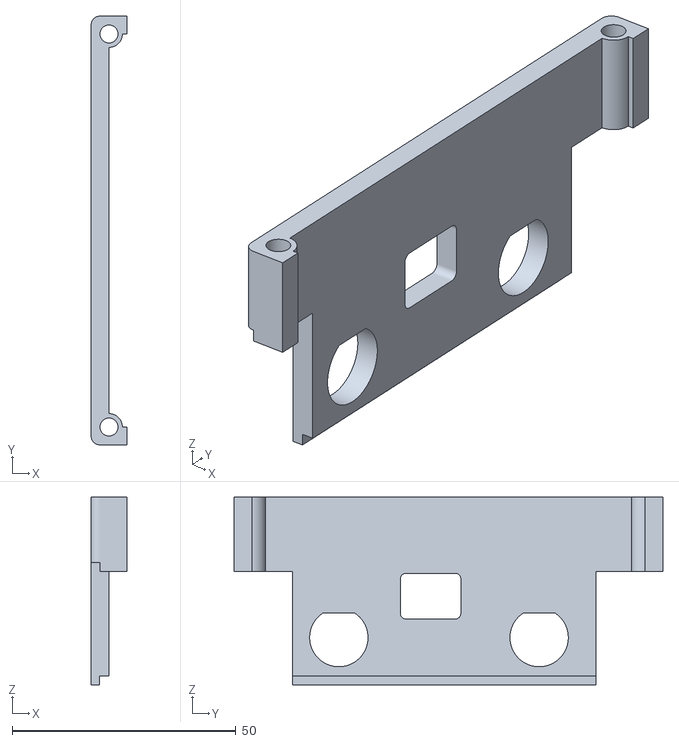
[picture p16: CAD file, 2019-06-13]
3D Designs/Stimulator/STL Files/Left.stl
8.00 x 95.8 x 42.0

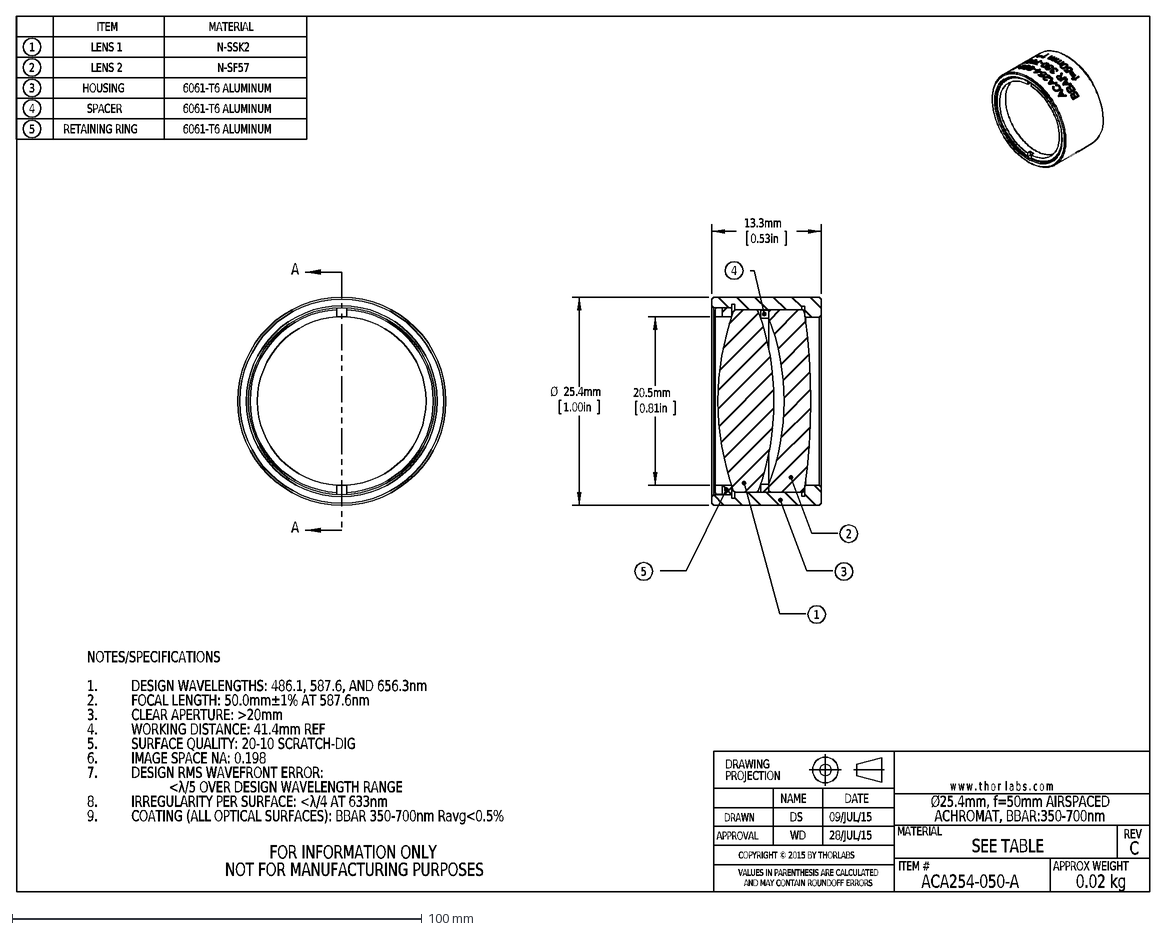
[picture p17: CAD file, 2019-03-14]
Datasheets/Optical components/Optics/50mm Achromatic Doublet lens/ACA254-050-A-AutoCADDXF.dxf
C
ACA254-050-A
MATERIAL
DRAWN
APPROVAL
REV
DS
WD
09/JUL/15
DATE
28/JUL/15
w w w . t h o r l a b s . c o m
ITEM #
APPROX WEIGHT
SEE TABLE
0.02 kg
VALUES IN PARENTHESIS ARE CALCULATED
AND MAY CONTAIN ROUNDOFF ERRORS
DRAWING
PROJECTION
NAME
FOR INFORMATION ONLY
NOT FOR MANUFACTURING PURPOSES
Ø25.4mm, f=50mm AIRSPACED
ACHROMAT, BBAR:350-700nm
COPYRIGHT © 2015 BY THORLABS
NOTES/SPECIFICATIONS
DESIGN WAVELENGTHS: 486.1, 587.6, AND 656.3nm
1.
FOCAL LENGTH: 50.0mm±1% AT 587.6nm
2.
CLEAR APERTURE: >20mm
3.
WORKING DISTANCE: 41.4mm REF
4.
SURFACE QUALITY: 20-10 SCRATCH-DIG
5.
IMAGE SPACE NA: 0.198
6.
DESIGN RMS WAVEFRONT ERROR:
7.
<λ/5 OVER DESIGN WAVELENGTH RANGE
IRREGULARITY PER SURFACE: <λ/4 AT 633nm
8.
COATING (ALL OPTICAL SURFACES): BBAR 350-700nm Ravg<0.5%
9.
ITEM
1
LENS 1
N-SSK2
2
LENS 2
N-SF57
3
HOUSING
6061-T6 ALUMINUM
4
SPACER
5
RETAINING RING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

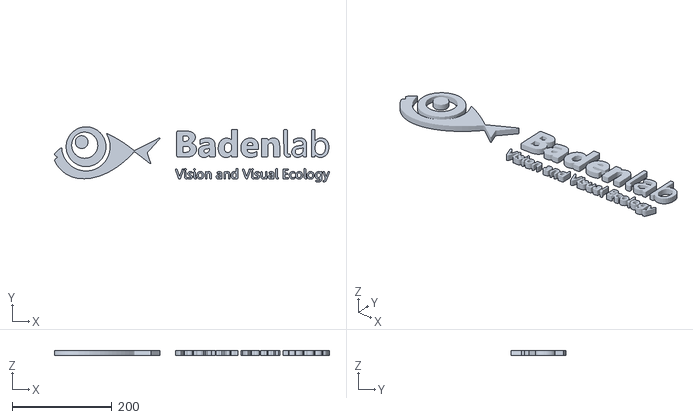
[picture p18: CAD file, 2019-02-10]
Images/Logo/Badenlab_logo.stl
550.3 x 111.0 x 10.0

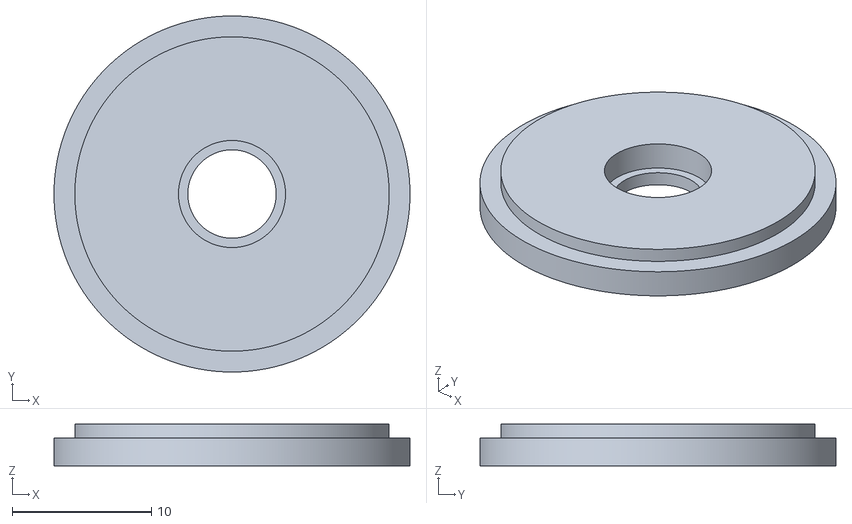
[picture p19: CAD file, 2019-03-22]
3D Designs/Optical Components/STL Files/1_LED_Holder.stl
25.6 x 25.6 x 3.00

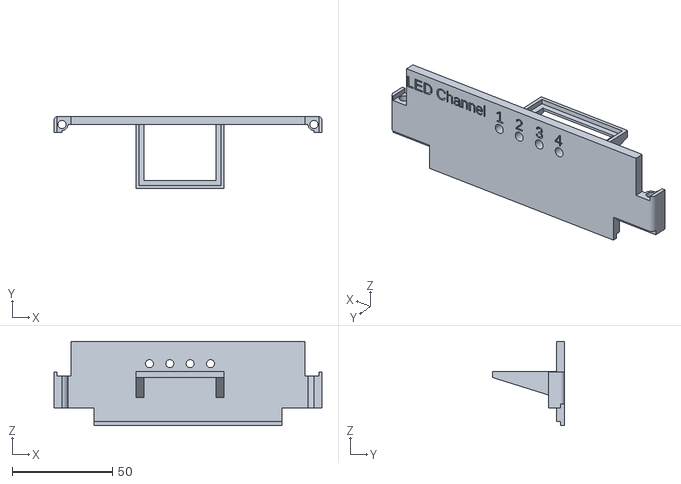
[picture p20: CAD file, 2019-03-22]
3D Designs/Stimulator/STL Files/Back.stl
133.8 x 36.0 x 42.0

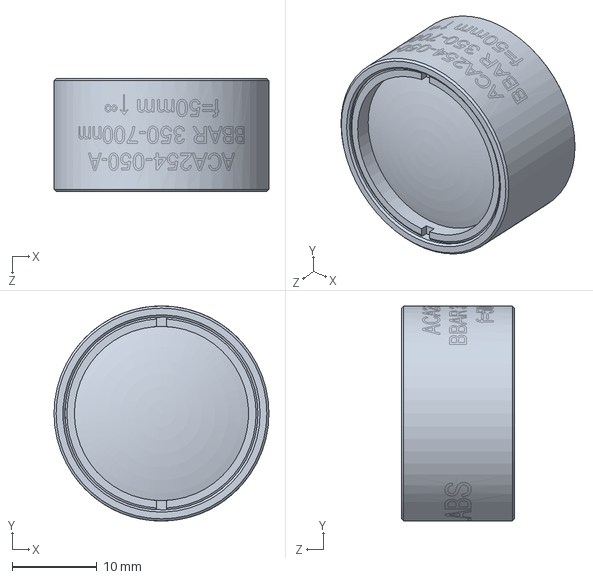
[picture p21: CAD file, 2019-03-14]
Datasheets/Optical components/Optics/50mm Achromatic Doublet lens/ACA254-050-A-Solidworks.sldprt
25.4 x 25.4 x 13.3 mm

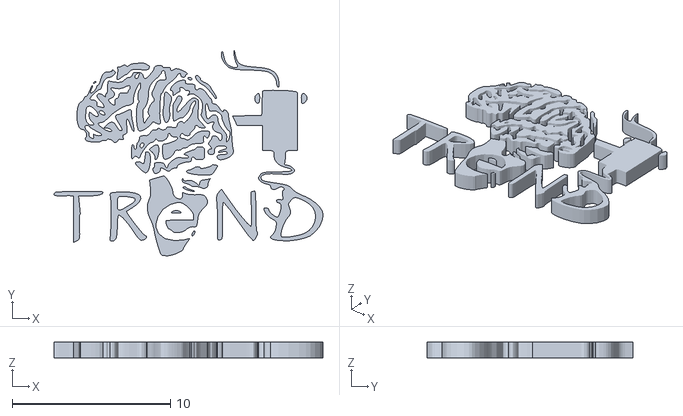
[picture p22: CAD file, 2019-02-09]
Images/Logo/Trend.stl
17.0 x 13.0 x 1.00

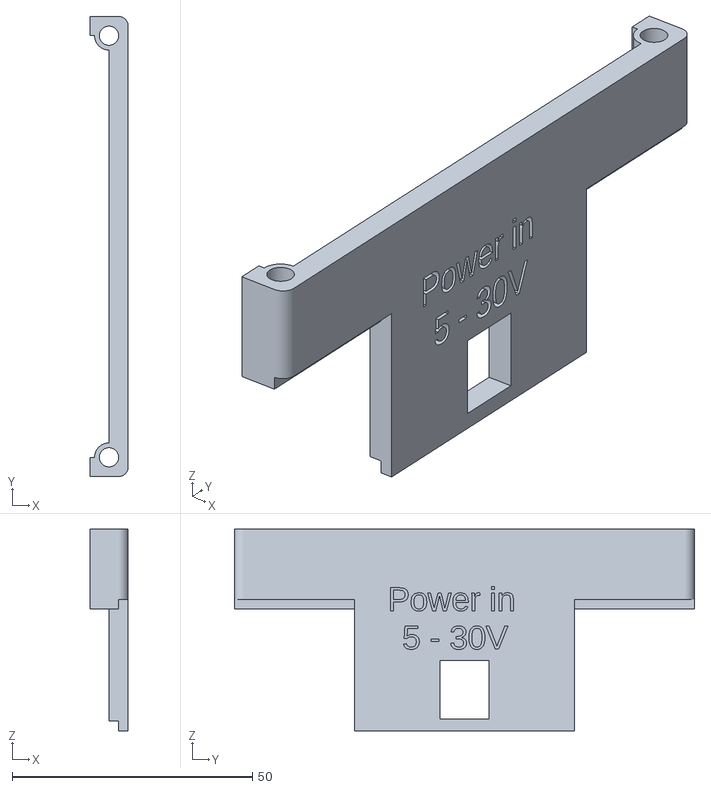
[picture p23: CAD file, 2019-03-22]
3D Designs/Stimulator/STL Files/Right.stl
8.00 x 95.8 x 42.0

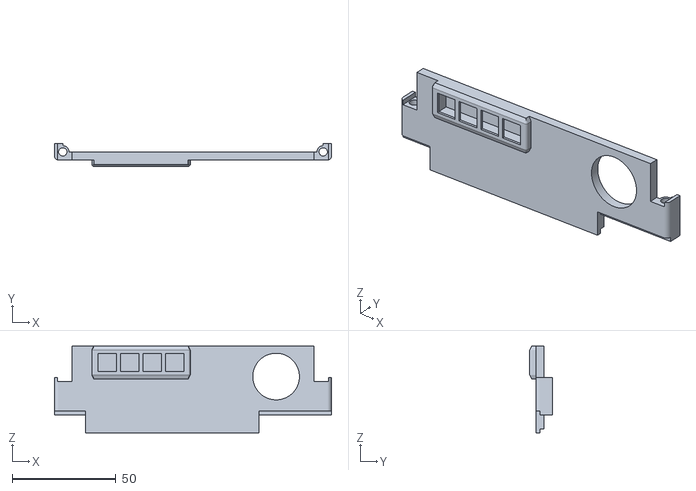
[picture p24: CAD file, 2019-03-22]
3D Designs/Stimulator/STL Files/Front.stl
133.8 x 11.0 x 42.0

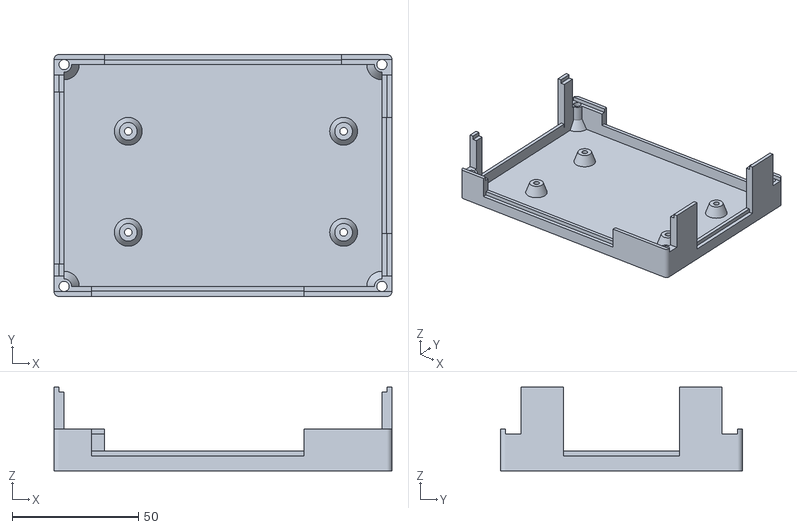
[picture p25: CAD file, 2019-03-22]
3D Designs/Stimulator/STL Files/Bottom.stl
133.8 x 95.8 x 33.2

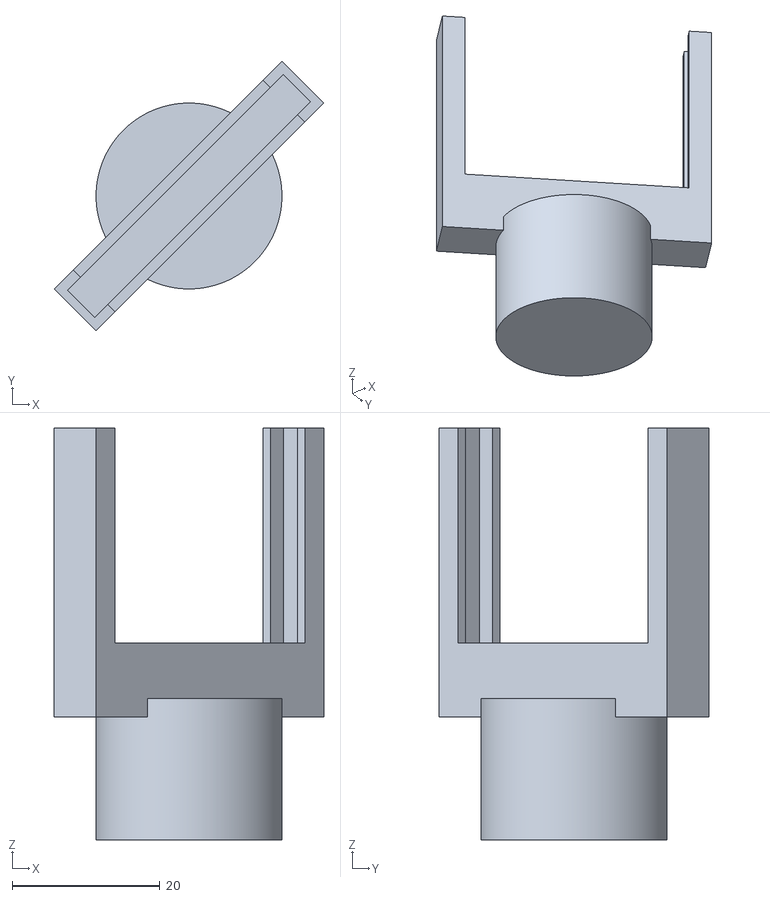
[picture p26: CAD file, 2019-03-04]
3D Designs/Optical Components/STL Files/dichroic_holder.stl
36.6 x 36.6 x 55.9

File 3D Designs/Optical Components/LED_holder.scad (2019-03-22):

/* 
                 LED Holder design to fit into a Thorlab 1 inch diameter lens holder
                            
        This holder has been designed to fit into the stimulator described in:
        Multi LED Stimulator v2.1: An opensource LED stimulator for visual and optogenetics 
        stimulation in combination with 2-photon recording

This project is Open Source licensed, released under CERN OHL v1.2

by M.J.Y. Zimmermann, 2018.12.11
Baden Lab, CRPC, School of Life Sciences, University of Sussex, United Kingdom



// // // // // // // // // // // // // // // // // // // // // // // // // // // // //
/*                            ---  User Parameters  ---                             */

Wall = 2;           // Defines the wall thickness of the box
Smoothness = 360;   // Number of facets
tol = 0.1;          // Printing tolerance

// // // // // // // // // // // // // // // // // // // // // // // // // // // //
/*                               ---  Switches  ---                              */

n_LED = 1;          // Determine the number of LEDs to mount (from 1 to 7)


// // // // // // // // // // // // // // // // // // // // // // // // // // // //
// // // // // // // // // // // // // // // // // // // // // // // // // // // //
/*                        ---  Component Parameters  ---                        */

r_lens_1_inch    = 25.8/2;      // ThorLabs 1 inch diameter lens radius
r_inner_ring     = 22.8/2;      // ThorLabs 1 inch diameter lens ring radius
h_ring           = 2;           // ThorLabs 1 inch diameter lens ring heigh

r_LED            = 6.35/2;      // 5mm LED radius
h_LED_Holder     = 3;
d_LED_Holder     = 8;           // 5mm LED clip diameter
h_clip           = 1;           // inside 5mm LED clip heigh
r_Clip           = 7.5/2+tol;   // 5mm LED clip radius



// // // // // // // // // // // // // // // // // // // // // // // // // // // //
/*                               ---  Display  ---                               */

difference(){
    LED_holder();
    
    if (n_LED==1){
        LED_hole();
    }
    if (n_LED==2){
        for (a=[0:180:360])rotate([0,0,a])translate([0,7,0])LED_hole();
    }
    if (n_LED==3){
        for (a=[0:360/3:360])rotate([0,0,a])translate([0,d_LED_Holder,0])LED_hole();
    }
    if (n_LED==4){
        LED_hole();
        for (a=[0:360/3:360])rotate([0,0,a])translate([0,d_LED_Holder,0])LED_hole();
    }
    if (n_LED==5){
        LED_hole();
        for (a=[0:360/4:360])rotate([0,0,a])translate([0,d_LED_Holder,0])LED_hole();
    }
    if (n_LED==6){
        LED_hole();
        for (a=[0:360/5:360])rotate([0,0,a])translate([0,d_LED_Holder,0])LED_hole();
    }
    if (n_LED==7){
        LED_hole();
        for (a=[0:360/6:360])rotate([0,0,a])translate([0,d_LED_Holder,0])LED_hole();
    }
}


// // // // // // // // // // // // // // // // // // // // // // // // // // // //
/*                               ---  Modules  ---                               */

module LED_holder(){
    difference(){
        cylinder(r=r_lens_1_inch-tol, h=h_LED_Holder, $fn=Smoothness);
    
        translate([0,0,h_ring])difference(){
            cylinder(r=r_lens_1_inch, h=h_LED_Holder, $fn=Smoothness);
            cylinder(r=r_inner_ring-tol, h=h_LED_Holder, $fn=Smoothness);
        }
    } 
}

module LED_hole(){
    cylinder(r=r_LED, h=h_LED_Holder, $fn=Smoothness);
    translate([0,0,h_clip])cylinder(r=r_Clip,h=h_LED_Holder,$fn=Smoothness);
}

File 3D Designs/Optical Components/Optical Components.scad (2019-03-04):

/* 

                            Optical Component parts for
                            Multi LED Stimulator v2.1.
                    
        An opensource LED stimulator for visual and optogenetics stimulation in combination with 2-photon recording



This 3D file is designed to be used along ThorLabs optical cage assemblies 

Source : https://github.com/BadenLab/Multi-Chromatic-Stmulator
This project is Open Source licensed, released under CERN OHL v1.2

by M.J.Y. Zimmermann and A.M. Chagas, 2019.02.25
Baden Lab, CRPC, School of Life Sciences, University of Sussex, United Kingdom

                                                                                     */


// // // // // // // // // // // // // // // // // // // // // // // // // // // // //
/*                            ---  User Parameters  ---                             */

Smoothness = 360;        // Number of facets. A value of 360 is recommended for a smooth print
tol = 0.1;               // Tolerance value, set by default to 0.1 for Ultimaker2 printer
Wall = 2.5;              // Wall thickness (applied only to certain modules)
wall = 2;                // Wall thickness (applied only to certain modules

// // // // // // // // // // // // // // // // // // // // // // // // // // // //
// // // // // // // // // // // // // // // // // // // // // // // // // // // //
/*                               ---  Switches  ---                              */
        LCP30 = 1;
        Mirror_Holder = 1;
        Dichroic_Frame = 1;


// // // // // // // // // // // // // // // // // // // // // // // // // // // // //
/*                         ---  Display Parameters  ---                             */

rotation = 45;      // mirror angle 
lens_offset = 1;
sep = 5;            // Separtion between objects (75 by default for proper display)


// // // // // // // // // // // // // // // // // // // // // // // // // // // //
// // // // // // // // // // // // // // // // // // // // // // // // // // // //
/*                        ---  Component Parameters  ---                        */

rod_pos2 = 60/2;         // Rod position for 60mm cage system
r_rod = 6.1/2 + tol/2;   // Rod radius 0.25 inch
S4 = 2.75/2;             // ThorLabs small holding screws 0.05 inch
r_lens_1_inch = 25.4/2;  // ThorLabs 1 inch Lens

Frame_Base = 10;
dichz = 25.4;
dichy = 1;
dichx = 36.2;

x_Frame = 36.2;
y_Frame = 3;
z_Frame = 25.4+1.5*Wall;
X_LCP30 = 73.7; //outer cube length
x_LCP30 = 40.7; //inner cube length
y_LCP30 = 40.6;
z_LCP30 = 12.70; //module thickness
y_Groove_LCP30 = 12.9;
x_arm_LCP30 = 16.5; //arm width
y_arm_LCP30 = 14; //arm length
x_ext_LCP30 = 96.3; //module diagonal length
pos_z_Screw_LCP30 = 5.6;
pos_x_screw_LCP30 = 67.3/2;
pos_y_screw_LCP30 = 26.7/2;

h_add=4;


 // // // // // // // // // // // // // // // // // // // // // // // // // // // //
/*                               ---  Display  ---                               */
if (LCP30==1){LCP();}
if (Mirror_Holder==1){translate([lens_offset,0,sep])rotate([0,0,rotation])mirror_holder();}
if (Dichroic_Frame==1){translate([lens_offset,0,z_LCP30+h_add+Frame_Base+2*sep])rotate([0,0,rotation])dich_frame();}


// // // // // // // // // // // // // // // // // // // // // // // // // // // //
/*                               ---  Modules  ---                               */

module LCP(){
difference(){
        union(){
            translate([-X_LCP30/2,-y_LCP30/2,0])cube([X_LCP30,y_LCP30,z_LCP30]);
             minkowski(){
                translate([-x_LCP30/2+2*tol+Wall,-y_LCP30/2+Wall,z_LCP30])cube([x_LCP30-2*tol-2*Wall,y_LCP30-2*Wall,h_add-Wall]);
                cylinder(r1=Wall,h=Wall,$fn=Smoothness);
            }
        }
        
        difference(){
           translate([-X_LCP30/2,-y_Groove_LCP30/2,0])cube([X_LCP30,y_Groove_LCP30,z_LCP30]);
           translate([-x_LCP30/2,-y_LCP30/2,0])cube([x_LCP30,y_LCP30,z_LCP30]);
        }
        
        Screw_LCP30();
        translate([lens_offset,0,0])cylinder(r=r_lens_1_inch,h=z_LCP30+h_add,$fn=Smoothness);
        
        //customisation
        translate([-X_LCP30/2,-y_LCP30/2,0])cube([X_LCP30/2-x_LCP30/2+2*tol,y_LCP30,z_LCP30]);
    }
    //customization
    difference(){
        
        translate([-X_LCP30/2,-y_Groove_LCP30/2+2*tol,0])cube([X_LCP30/2-x_LCP30/2+2*tol,y_Groove_LCP30-4*tol,z_LCP30]);
        
        Screw_LCP30();
        translate([-pos_x_screw_LCP30,0,0])cylinder(r=S4,h=z_LCP30,$fn=Smoothness);
    }
}

module Screw_LCP30(){ 
    translate([pos_x_screw_LCP30,pos_y_screw_LCP30,0])cylinder(r=S4,h=z_LCP30,$fn=Smoothness);
    translate([pos_x_screw_LCP30,-pos_y_screw_LCP30,0])cylinder(r=S4,h=z_LCP30,$fn=Smoothness);
    
    translate([rod_pos2,-y_LCP30/2,pos_z_Screw_LCP30])rotate([-90,0,0])cylinder(r=r_rod,h=y_LCP30,$fn=Smoothness);
    translate([-rod_pos2,-y_LCP30/2,pos_z_Screw_LCP30])rotate([-90,0,0])cylinder(r=r_rod,h=y_LCP30,$fn=Smoothness);
    
    
    translate([x_LCP30/2,0,z_LCP30+h_add/3])rotate([0,-90,0])cylinder(r=S4,h=x_LCP30/2,$fn=Smoothness);
    translate([x_LCP30/2,0,h_add+3])rotate([0,-90,0])cylinder(r=S4,h=x_LCP30/2,$fn=Smoothness);
    translate([0,x_LCP30/2,z_LCP30+h_add/3])rotate([90,0,0])cylinder(r=S4,h=x_LCP30/2,$fn=Smoothness);
    translate([0,-x_LCP30/2,z_LCP30+h_add/3])rotate([-90,0,0])cylinder(r=S4,h=x_LCP30/2,$fn=Smoothness);
}

module mirror_holder(){
cylinder(r=r_lens_1_inch-tol,h=z_LCP30+Wall+h_add,$fn=Smoothness);
    
translate([0,0,z_LCP30+h_add])difference(){
    translate([-x_Frame/2-1.5*Wall,-y_Frame/2-Wall,0])cube([x_Frame+3*Wall,y_Frame+2*Wall,z_Frame+Frame_Base]);
    
    translate([-x_Frame/2-tol,-y_Frame/2-Wall,Frame_Base])cube([x_Frame+2*tol,y_Frame+2*Wall,z_Frame+tol]);
    translate([-x_Frame/2-Wall-tol,-y_Frame/2-wall/2-tol,Frame_Base-Wall/2])cube([x_Frame+2*Wall+2*tol,y_Frame+wall+2*tol,z_Frame+Wall/2+tol]);
}
}

module dich_frame(){
difference(){    
    translate([-x_Frame/2-Wall,-y_Frame/2-wall/2,0])cube([x_Frame+2*Wall,y_Frame+wall,z_Frame]);

    translate([-dichx/2-tol,-y_Frame/2-wall/2,Wall-tol])cube([dichx+2*tol,dichy+wall/2,dichz+2*tol]);
    translate([-dichx/2+wall/2,-y_Frame/2-Wall,Wall-tol+wall/2])cube([dichx-wall,y_Frame+2*wall,dichz-wall]);
    translate([-Wall,-y_Frame/2-wall/2,z_Frame-Wall])cube([2*wall,dichy+wall/2,Wall]);
}
}

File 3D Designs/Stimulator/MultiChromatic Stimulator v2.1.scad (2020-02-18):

/* 

                            Multi LED Stimulator v2.1.
                    
        An opensource LED stimulator for visual and optogenetics stimulation in combination with 2-photon recording



This 3D file is designed for the Multi-Chromatic Stimulator project components and its customed PCB
Source : https://github.com/BadenLab/Multi-Chromatic-Stmulator
This project is Open Source licensed, released under CERN OHL v1.2

by M.J.Y. Zimmermann, 2018.12.11
Baden Lab, CRPC, School of Life Sciences, University of Sussex, United Kingdom

                                                                                     */



// // // // // // // // // // // // // // // // // // // // // // // // // // // // //
/*                            ---  User Parameters  ---                             */
 
Wall = 2;           // Defines the wall thickness of the box
Smoothness = 360;   // Number of facets
tol = 0.1;          // Printing tolerance
TOL = 0.4;          // Component tolerance

sep = 7;            // x & y separation values for display function
zsep = 7;           // z separation values for display function


// // // // // // // // // // // // // // // // // // // // // // // // // // // //
// // // // // // // // // // // // // // // // // // // // // // // // // // // //
/*                               ---  Switches  ---                              */

Bottom = 1;
Front = 1;
Right = 1;
Left = 1;
Back = 1;
Lid = 1;

LED_Option = 1;
LED_Holder = 1;

PCB = 10;
Power_Switch = 10;

// // // // // // // // // // // // // // // // // // // // // // // // // // // //
// // // // // // // // // // // // // // // // // // // // // // // // // // // //
/*                        ---  Component Parameters  ---                        */
// Customed PCB
    x_PCB = 125;
    y_PCB = 75;
    z_PCB = 1;
    
// Box
    x_Box = x_PCB + 2*TOL;
    y_Box = y_PCB + 2*TOL + 6*Wall;
    z_Box = 50; 
    
// Number of LED channel
    n_LED = 4;          

// Potentiometer Board
    x_pot = 40;
    y_pot = 30;
    z_pot = 6.86+z_PCB;
    z_pot2 = 4.9+z_PCB;
    d_pot = 10.26;
    r_pot = 3/2+tol;
    pot_pitch = 2.54*4;
    pos_z_pot = z_Box-20;
    x_Support = 2*Wall;
    z_Support = 5*Wall;
    y_Support = sqrt((y_pot+Wall)*(y_pot+Wall)+z_Support*z_Support);
    rotate_Support = [atan((y_pot+Wall)/z_Support),0,0];
    
// M3
    r_M3 = 3/2;
    R_M3 = 4/2;
    r_M3_Nut = 6.44/2;
    h_M3_Nut = 2.3;
    
// M4
    r_M4 = 4/2;
    R_M4 = 6.85/2;
    r_M4_Nut = 7.8/2;
    h_M4_Nut = 2.1;
    
 
    pos_x_PCB1 = -x_PCB/2 + 25+2*Wall;
    pos_x_PCB2 = -x_PCB/2 + 110.25+2*Wall;
    pos_y_PCB1 = -y_PCB/2 + 15+2*Wall;
    pos_y_PCB2 = -y_PCB/2 + 55+2*Wall;
    pos_z_PCB = 7.5;
    
// BNC
    pos_y_BNC1 = 13+2*Wall;
    pos_y_BNC2 = 57.75+2*Wall;
    pos_z_BNC2 = 15.8/2;
    h_BNC = 15.8/2;
    r_BNC = 12.83/2;
    cut_BNC = r_BNC-5.54;
    pos_z_BNC = pos_z_PCB + z_PCB + pos_z_BNC2 + 2*tol;
    
// Barrel Jack
    h_Jack = 11.15 + 2*tol;
    y_Jack = 9.25 + 2*tol;
    pos_y_Jack = 47.75;
    
// USB
    y_USB = 10.8;
    z_USB = 7.7;
    pos_z_USB = pos_z_PCB + z_PCB + 12.25+1.25;
    
// Box
    f1=15;
    f2=x_Box+4*Wall-f1-35;  
    b1=20;
    b2=x_Box+4*Wall-b1-20;
    r1=25;
    r2=y_Box+4*Wall-r1-25;
    l1=13;
    l2=y_Box+4*Wall-l1-15;
    
// LEDs
    r_LED = 4.75/2 + tol;
    R_LED = 3/2;
    x_LED = 2*R_LED + 2.5*Wall;
    d_LED = 10;
    pos_LED = [-x_Box/2+f1+2*Wall,-y_Box/2-Wall,z_Box/2+15.05];
    h_Sheet = 0.3;
    z_Sheet = Wall - h_Sheet;
    r_Cable = 15/2;

// Connectors
    x_connector = 7.5;
    x_connector2 = 10;
    y_connector = 6;
    z_connector = 15;

// Adafruit TLC
    x_TLC = 51.3;
    y_TLC = 25.5;
    z_TLC = 12.75;

//Adafruit ESP32 Feather HUZZAH   
    x_ESP = 51;
    y_ESP = 23;
    z_ESP = 12.75;
     
// Power Switch
    r_Switch = 20.5/2+tol;
    x_Switch = 10.75;
    y_Switch = 22.5;
    z_Switch = 15;
    pos_z_Switch = 22.5;
    
// Screws
    pos_x_Screw1 = -x_Box/2+2*Wall;
    pos_x_Screw2 = x_Box/2+2*Wall;
    pos_y_Screw1 = -y_Box/2+2*Wall;
    pos_y_Screw2 = y_Box/2+2*Wall;
    

 // // // // // // // // // // // // // // // // // // // // // // // // // // // //
/*                               ---  Display  ---                               */

if(Bottom==1){
    difference(){
        Box();
        
        translate([-x_Box/2-tol,-y_Box/2-tol,z_Box-Wall-2*tol])cube([x_Box+4*Wall+2*tol,y_Box+4*Wall+2*tol,2*Wall+4*tol]);
        Front_neg();
        Back_neg();
        Left_neg();
        Right_neg();  
    }
}
if(Front==1){translate([0,-sep,zsep]){
    difference(){
        intersection(){
            Box();
            Front();
        }
        Right_neg();
        Left_neg();
    }
    if (LED_Option==1)LED();
}}
if(Back==1){translate([0,sep,zsep]){
    difference(){
        intersection(){
            Box();
            Back();
        }
        Right_neg();
        Left_neg();
        Potentiometer();
    }
    Potentiometer_Platform();
}}
if(Right==1){translate([sep,0,2*zsep]){
    difference(){
        intersection(){
            Box();
            Right();
        }
    }
}}

if(Left==1)translate([-sep,0,2*zsep]){
    difference(){
        intersection(){
            Box();
            Left();
        }
    }
}

if(Lid==1)translate([0,0,3*zsep+tol]){
    difference(){
        union(){
            Lid();
            Box();
        }
        Top_neg();
        Screws();
        Logo();
        Labels();
    }
}

if(LED_Holder==1)translate([0,sep,0]){
    LED_Holder();
}

if(PCB==1){
    color([0,1,0])PCB();
}
if(Power_Switch==1){
    color([0,0,1])Switch();
}

// // // // // // // // // // // // // // // // // // // // // // // // // // // //
/*                               ---  Modules  ---                               */
   

module Box(){
   difference(){
       minkowski(){
           translate([-x_Box/2+Wall,-y_Box/2+Wall,0])cube([x_Box+2*Wall,y_Box+2*Wall,z_Box-Wall]);
           cylinder(r1=Wall,h=Wall,$fn=Smoothness);
       }
       difference(){
           translate([-x_Box/2+2*Wall,-y_Box/2+2*Wall,Wall])cube([x_Box,y_Box,z_Box+tol]);
           Corners();
       }
       Screws();
       Nuts();
       BNC();
       Jack();
       USB();
       Power_Switch();
       Labels();
       if (LED_Option==1)LED_neg();
       LED_Cables();
   }
   
    Platform();
    
   
}

module Lid(){
   difference(){
      translate([-x_Box/2+2*Wall,-y_Box/2+2*Wall,z_Box-2*Wall])cube([x_Box,y_Box,2*Wall]);
  } 
}

module PCB(){
    translate([-x_PCB/2,-y_PCB/2,pos_z_PCB])cube([x_PCB,y_PCB,z_PCB]);
    for (aa = [0:10:110]){
        translate([-x_PCB/2+aa,-y_PCB/2+0.5,pos_z_PCB+z_PCB])cube([x_connector,y_connector,z_connector]);
    }
    for (bb = [0:10:110]){
        translate([-x_PCB/2+bb,y_PCB/2-0.5-y_connector,pos_z_PCB+z_PCB])cube([x_connector,y_connector,z_connector]);
    }
    for (aaa = [126.5:10:186.5]){
        translate([-x_PCB/2+aaa,-y_PCB/2+0.5,pos_z_PCB+z_PCB])cube([x_connector,y_connector,z_connector]);
    }
    for (bbb = [126.5:10:186.5]){
        translate([-x_PCB/2+bbb,y_PCB/2-0.5-y_connector,pos_z_PCB+z_PCB])cube([x_connector,y_connector,z_connector]);
    }
    
    translate([x_PCB/2-0.5-y_connector,-y_PCB/2+11.7,pos_z_PCB+z_PCB])cube([y_connector,x_connector,z_connector]);
    translate([x_PCB/2-0.5-y_connector,-y_PCB/2+23.25,pos_z_PCB+z_PCB])cube([y_connector,x_connector2,z_connector]);
    translate([x_PCB/2-0.5-y_connector,-y_PCB/2+47.6,pos_z_PCB+z_PCB])cube([y_connector,x_connector,z_connector]);
    translate([x_PCB/2-0.5-y_connector,-y_PCB/2+59.4,pos_z_PCB+z_PCB])cube([y_connector,x_connector,z_connector]);
    
    translate([x_PCB/2-15+2,-y_PCB/2+34.75,pos_z_PCB+z_PCB])cube([15,y_Jack,h_Jack]);
    

     
     translate([-x_PCB/2+56.5,-y_PCB/2+25,pos_z_PCB+z_PCB])cube([x_TLC,y_TLC,z_TLC]);
    translate([-x_PCB/2+128,-y_PCB/2+25,pos_z_PCB+z_PCB])cube([x_TLC,y_TLC,z_TLC]);
     
     translate([-x_PCB/2,-y_PCB/2+23.5,pos_z_PCB+z_PCB])cube([x_ESP,y_ESP,z_ESP]);
}

module Platform(){
    difference(){
        union(){
            translate([pos_x_PCB1,pos_y_PCB1,Wall])cylinder(r1=r_M3+2*Wall,r2=r_M3+Wall,h=pos_z_PCB-Wall,$fn=Smoothness);
            translate([pos_x_PCB1,pos_y_PCB2,Wall])cylinder(r1=r_M3+2*Wall,r2=r_M3+Wall,h=pos_z_PCB-Wall,$fn=Smoothness);
            translate([pos_x_PCB2,pos_y_PCB1,Wall])cylinder(r1=r_M3+2*Wall,r2=r_M3+Wall,h=pos_z_PCB-Wall,$fn=Smoothness);
            translate([pos_x_PCB2,pos_y_PCB2,Wall])cylinder(r1=r_M3+2*Wall,r2=r_M3+Wall,h=pos_z_PCB-Wall,$fn=Smoothness);
        }
        Screws();
        Nuts();
    }
}
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

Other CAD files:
3D Designs/Optical Components/STL Files/7_LED_Holder.stl
Datasheets/Optical components/Optics/50mm Achromatic Doublet lens/ACA254-050-A-Step.step
3D Designs/Optical Components/STL Files/4_LED_Holder.stl
3D Designs/Optical Components/STL Files/5_LED_Holder.stl
3D Designs/Optical Components/STL Files/3_LED_Holder.stl
3D Designs/Optical Components/STL Files/2_LED_Holder.stl
3D Designs/Optical Components/STL Files/dichroic_frame.stl

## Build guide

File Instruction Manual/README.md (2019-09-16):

<p align="right">
<h1 align="center">Instruction Manual</h1></p>
<h1 align="center">Multi-Chromatic Stimulator</h1>

***

## Overview



This document contains detailed assembly instructions, a software guideline to customize stimuli, and includes a parts list.

 The Arduino code and 3D printing files (SCAD and STL) can be downloaded [here](https://github.com/BadenLab/Tetra-Chromatic-Stimulator/tree/master/3D%20Designs), and further modified to fit customise purposes. The aim of this device is to finely control LEDs used in combination with a 2-photon microscope.

The device consists of a custom-designed PCB, an [ESP32 development board](https://learn.adafruit.com/adafruit-huzzah32-esp32-feather) (or an Arduino Nano if the stimulator does not need to be combined with a 2 photon microscope), a [LED driver](https://learn.adafruit.com/tlc5947-tlc59711-pwm-led-driver-breakout/overview) and various off-the-shelf components.

***

- [Assembling the Stimulator](#Assembling-the-Stimulator)
- [Programming the Stimulator](#Programming-the-ESP32)
- [Operating the Stimulator](#Operating-the-Stimulator)
- [Calibrating the Stimulator](#Calibrating-the-Stimulator)

***

## Assembling the stimulator



<p align="center"><h4 align="left">1 – Obtaining the custom-designed PCB</h4></p>

From the GitHub repository, one can find the [gerber.zip folder](https://github.com/BadenLab/Tetra-Chromatic-Stimulator/tree/master/PCB/Stimulator) needed to order the PCB to any manufacturer company (i.e. https://jlcpcb.com).

Ordering a minimum of five units should not cost more than £10. Gerber files were designed with [KiCad 5.0](http://kicad-pcb.org/).

Schematics and PCB footprint can be downloaded and modified from the same repository if need be.

****

<p align="center"><h4 align="left">2 – Soldering the custom-designed PCB</h4></p>
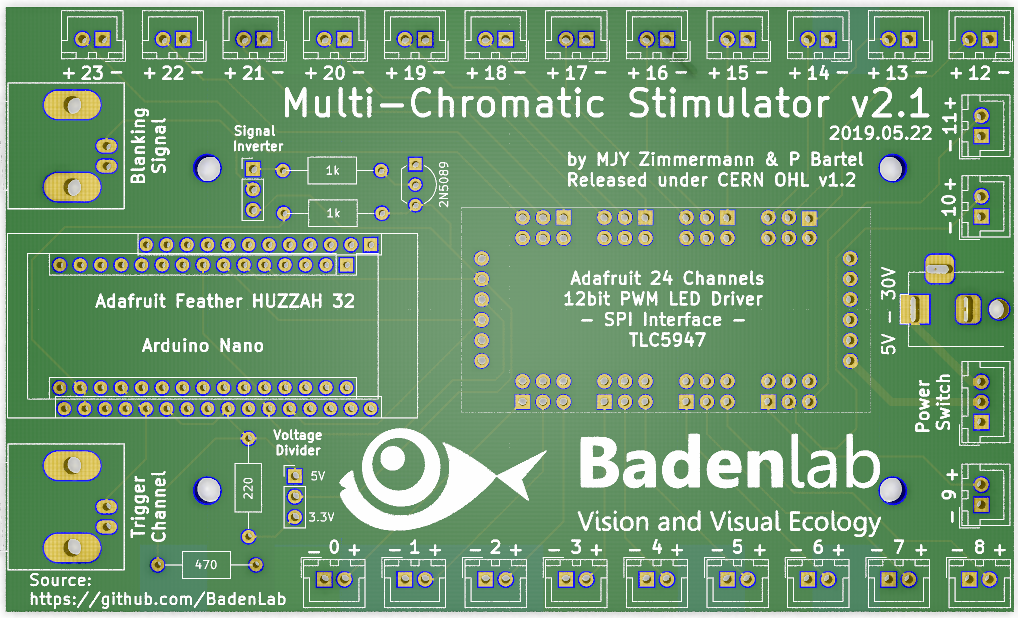
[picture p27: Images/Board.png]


The board is self-explanatory. On the left, two options are available, one for the Arduino (close rows) the other for the ESP (spread rows). There is no need to solder more JST pins that the number of LED required for the desired stimulator.

The jumper on the top (Signal Inverter) allows the inversion of the TTL "Blanking" signals. For ScanImage users, the jumper should be placed at the upper position.

The jumper at the bottom of the board (Voltage Divider) allows to tune down the voltage from 5 to 3.3V if the ESP is used instead of an Arduino. ESP32 unlike Arduino Nano, works on a 3.3V logic; no higher tension should be sent to this board. Since most TTL deliver 5V pulses, we selected a 220/470Ω divider to bring a 5V blanking signal into a 3.3V input. Depending on the blanking signal generator used, this divider can be modified to fit one’s personal design or bypassed by only bridging the 220Ω resistor.

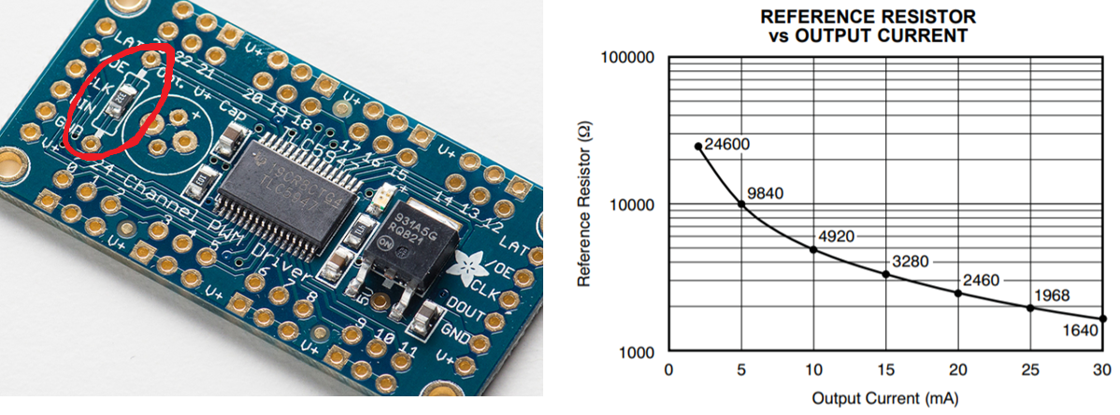
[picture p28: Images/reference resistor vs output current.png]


The Adafruit TLC5947 LED driver is a constant current driver configured by default to set the current level at 15mA per channel, which is virtually safe for any LED. However, one can operate at different current by replacing the on-board reference resistor with a through hole resistor. The driver is capable to deliver up to 30mA, the graph below shows the relationship between resistance and output current.

****

<p align="center"><h4 align="left">3 – Mounting the potentiometer</h4></p>
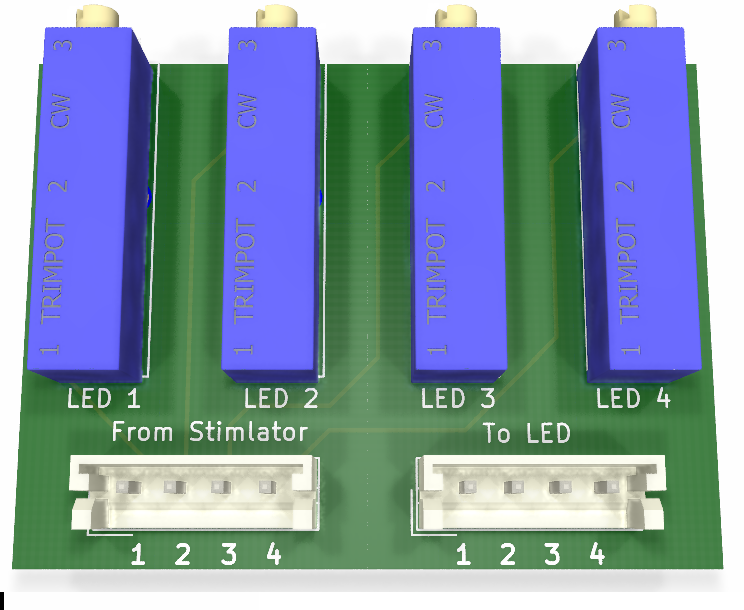
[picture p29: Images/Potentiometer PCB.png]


In order to finely adjust each LED power, we added multiple-turn trimmer potentiometers to our design. A simple solution is to manufacture the appropriate PCB board (We provide multiple options on the [GitHub repository](https://github.com/BadenLab/Tetra-Chromatic-Stimulator/tree/master/PCB/Potentiometer%20Mounts)).

Otherwise, one can make its own little PCB by using a solderable board.
Each potentiometer connects its ClockWise (pin 3) to the LED (+) stimulator JST pin; and its Base (pin 2) to the LED (+) leg. The LED (-) stimulator JST pin connects the LED (-) leg directly.

***

<p align="center"><h4 align="left">4 – Printing the Stimulator box</h4></p>


[STL files](https://github.com/BadenLab/Tetra-Chromatic-Stimulator/tree/master/3D%20Designs/Stimulator/STL%20Files) can be found on the GitHub repository and print directly if the user wishes to go for the default design (4 stimulation LEDs + 4 proxy LEDs) and [BoM](https://github.com/BadenLab/Tetra-Chromatic-Stimulator/blob/master/Bills%20of%20Materials/BOM%20-%20Stimulator.ods).

However, [SCAD files](https://github.com/BadenLab/Tetra-Chromatic-Stimulator/blob/master/3D%20Designs/Stimulator/MultiChromatic%20Stimulator%20v2.1.scad) are also available and easily adjustable for personalised design.

We used [OpenSCAD](www.openscad.com) to design the stimulator box. The tolerance of the printer can be adjusted in the “USER Parameters” section of the script (tol =0.1; by default, this value is used for Prusa MK3 and Ultimaker 2). Each component can be displayed/design individually in the “Switches” section. Variables such as LED number (4 by default) and the potentiometer board dimensions can be adjusted in the “Component Parameters” section.

The PCB is screwed to the “Bottom” part of the box by using M3 screws and nuts. The potentiometer board adjusts itself with the “Back” part of the box, and the trimmers should adapt to their respective holes exactly.
All part should fit tightly together and are maintained together by 4 M3*50mm socket screws.

***

<p align="center"><h4 align="left">5 – Adjusting the proxy LED</h4></p>
The proxy LED are markers for the experimenter to have a ready visualisation of the stimulus being displayed under the objective. If this option is selected, 3mm LEDs are to be mounted at the back of the LED holder using 3mm LED mounts.

Finally, any translucid material could be placed in the LED holder slot in order to diffuse the proxy LED light (In our example, we used a piece of thin Teflon)

***

<p align="center"><h4 align="left">6 – Connecting the Stimulator</h4></p>
The stimulator can be powered from 5 to 30v. The Adafruit TLC5947 being a constant current LED driver, the voltage selection is not critical, however it has to be slightly higher than the LED forward voltage (LED datasheet). Multiple LEDs can be connected to the same channel; however, the voltage supply has to be adjusted in consequence. For example, if an LED has 3.2v forward voltage, then a power supply => 3.2v will be enough, however if 5 of those LEDs are connected in series to the same channel, then the power supply has to be => 3.2v * 5 => 16v.

Blanking signal BNC has to be connected to a TTL (pulse generator), that delivers 5V pulses (if voltage is different, refer yourself to the soldering paragraph). Here we called blanking signal the pulse synchronised with the scanning mirror (scanning retrace), the laser Pockels cell and the PMTs. On our setup, when blanking signal is HIGH, the scanning mirror starts a new scanning line, the Pockels cell let the laser beam through, the PMT records the emitting fluorescence and the stimulating LEDs are turned off. When the blanking signal is LOW, the opposite occurs.

The trigger channel is an output signal generated by the stimulator that by default sends a 3.3v pulse (if ESP32 is used, 5v for Arduino nano) at the start of the stimulus and then at every 1.00000s. This trigger is used during the analysis to correlate the displayed stimulus to the fluorescence trace recordings.

Finally, the board is connected to a computer via micro USB cable (for ESP32, mini USB for Arduino Nano), and ready to be used.



***

## Programming the ESP32

1-	Download and install [Arduino environment](www.arduino.org) on the computer.

2-	To use the ESP32, a couple of steps are necessary
Install the latest SiLabs [CP2104 driver](https://www.silabs.com/products/development-tools/software/usb-to-uart-bridge-vcp-drivers).
Follow the installation instructions from the [Espressif repository](https://github.com/espressif/arduino-esp32/blob/master/docs/arduino-ide/boards_manager.md).

3-	Install the TLC5947 library:	Start Arduino and from the “Sketch” tab, select “Include Library” and open “ Manage Libraries”.	From the search bar enter “TLC5947”. Select and Install the library

4-	Close Arduino and open the Multi-Chromatic-Stimulator arduino file from the [Arduino Code folder](https://github.com/BadenLab/Tetra-Chromatic-Stimulator/tree/master/Arduino%20code/2-Photon_Mutli_Chromatic_Stimulator).

5-	From the “Tools” tab: Select from “Boards” the “Adafruit ESP32 Feather”.	From “Upload Speed”, select 921600.	From “Flash Frequency”, select 80Hz. From “Port”, select the computer port to which the ESP is connected (if doubt, unplug, replug and observe the choices differences). If the ESP is not recognised, check the driver installation (2), then check the micro USB cable.

6-	Compile and Upload the code by clicking on the arrow button on the top left.

7-	The stimulator is ready to be used.

***

## Operating the Stimulator
<p align="center"><h4 align="left">The code is organised in five distinct part:</h4></p>

  Stimulus Parameters

Here, users determine the sequence of their looping stimulus.

–	The *array_LED#* corresponds to the sequence of each LED#. The value corresponds to the LED power and CAN ONLY TAKE A VALUE FROM 0 TO 100, where 0 corresponds to no light and 100 to max light intensity

–	The *array_Time* corresponds to the duration of each entry in ms; the first entry being the pre-adaptation that will only be played at the start of the stimulus, the sequence will then loop starting at the second position.

–	The number of Loops is determined by *nLoops*. The stimulus will stop after finishing the n Loop.

–	IMPORTANT, for the code to work flawlessly, the number of entries within the arrays has to be the same and manually entered in nArrayEntries (including the pre-adaptation at position 1).

***

  Microcontroller Board Selection

This is where the user defines if he is using an ESP32 or an Arduino Nano

***

  Internal Definitions

This is the main definition part of the code which can be modified to:

-	Add more LEDs than the 4 main and 4 proxy defined by default. (Global variables, the LED pins correspond to the pin number on the TLC5947).

-	Adjust the Trigger duration (25ms by default). This value corresponds to the amount of time the trigger marker will remain on in order to be detected by i.e. a DAQ.

-	Adjust the Trigger interval (1000 ms by default). Value between two successive triggers.

***

  Internal Methods

This is the main core of the code and should not be structurally changed apart from adding more LEDs (straight forward)

***

  Main Loop

This is where the stimuli controls are defined. By default, when compile window is open (magnifying glass on the top right corner) and the baud rate at the bottom right of the window has be changed to 115200, a manual command will trigger a stimulus:

By default:

-	*a* –> Play stimulus at max power 1

-	*b* –> Play stimulus at max power 2

-	*0* –> Turn off all LEDs stop any stimulus being played and reset the loop

-	*+* –> Turn on all LED to max power 1

-	*-* –> Turn on all LED to max power 2

-	*1* –> Turn First LED to max power 1

-	*2* –> Turn First LED to max power 2

-	*3* –> Turn Second LED to max power 1

-	*4* –> Turn Second LED to max power 2

-	*5* –> Turn Third LED to max power 1

-	*6* –> Turn Third LED to max power 2

-	*7* –> Turn Fourth LED to max power 1

-	*8* –> Turn Fourth LED to max power 2

Important to note, obviously the stimulation will only be played if a blanking signal is sent to the board.

***

## Calibrating the Stimulator

The TLC5947 is a 12 bits PWM grayscale driver, meaning that it offers a 4096 degree of freedom to adjust each LED power.
On the arduino code there is a second tab called “LED_values” which hard-codes the maximum power a LED can get. Those values range from 0 (no current) to 4095 (max current, 15mA by default).

On the default script we proposed 2 distinct max values (named here max1 and max2 power) that can be called individually. The purpose here is to have the opportunity to use the same stimulus sequence at two different light intensities. Off course more can be added manually by the user.

For the calibration, we suggest setting the max_LED# value at 4095 (Full power), play the stimulus (while the board receives a blanking signal it sees its LED average light intensity decrease (LED off while blanking)) and jointly use a spectrometer and a powermeter.

### Visual Stimulator Calibration

For the visual stimulator, we used the [ThorLabs Compact CCD Spectrometer](https://www.thorlabs.com/newgrouppage9.cfm?objectgroup_ID=3482) CCS200/M in combination with the [ThorLabs OSA software](https://www.thorlabs.com/software_pages/ViewSoftwarePage.cfm?Code=OSA).
We placed the spectrometer fiber patch cable at the sample position and played the calibration code on the stimulator. This calibration sequence plays each LED individually from 0 to 100% for 1 second and loops 5 times. This stimulus sequence is quite tedious so we encourage users to adapt it to their needs.
Recordings were made using the inbuilt trigger mode of the spectrometer (connected to the stimulator trigger output). We used an integration time of 1 second and applied the inbuilt spectrum correction in the OSA software. Data was extracted as .csv files and analysed using our [iPython analysis script](https://github.com/BadenLab/Tetra-Chromatic-Stimulator/blob/master/Instruction%20Manual/Stimulator%20Calibration/Stimulator_Calibration.ipynb).

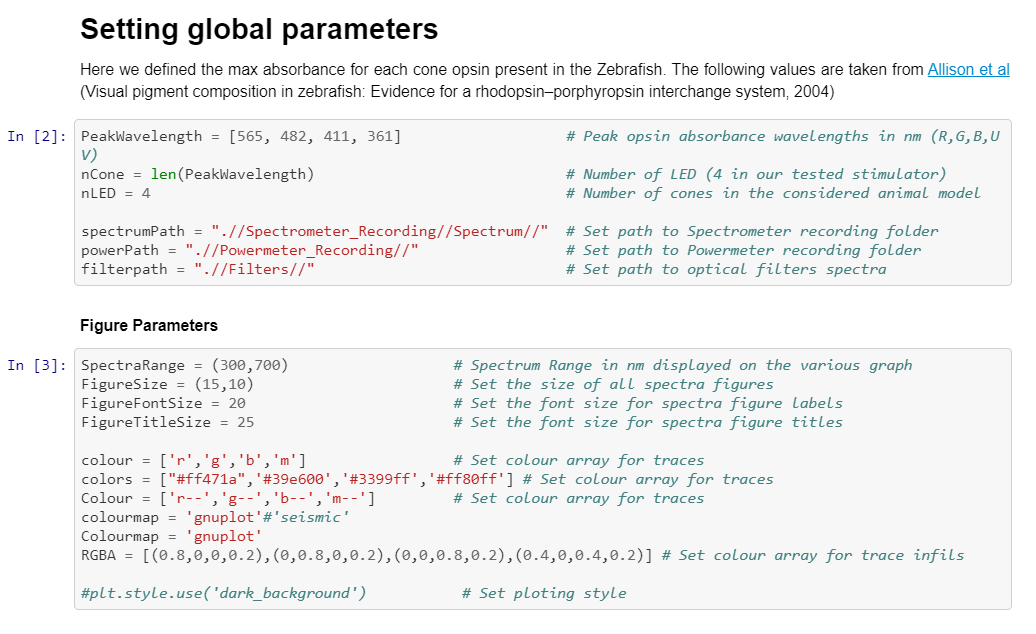
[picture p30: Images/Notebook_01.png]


For analysis purposes, we designed an [iPython notebook](https://jupyter.readthedocs.io/en/latest/install.html).
In this script, one has to first modify the global parameters:
  - Opsin maximum absorbance: *PeakWavelength* This array contains the peak asorbance for each opsin considered. For the zebrafish, we use the value defined by [Allison et al, 2004 - Visual pigment composition in Zebrafish](https://github.com/BadenLab/Tetra-Chromatic-Stimulator/blob/master/References/Allison%202004%20-%20Visual%20pigment%20composition%20in%20zebrafish.pdf)
  - Number of LEDs to be considered
  - Figure parameters: Figure sizes, spectra range to considered, etc.

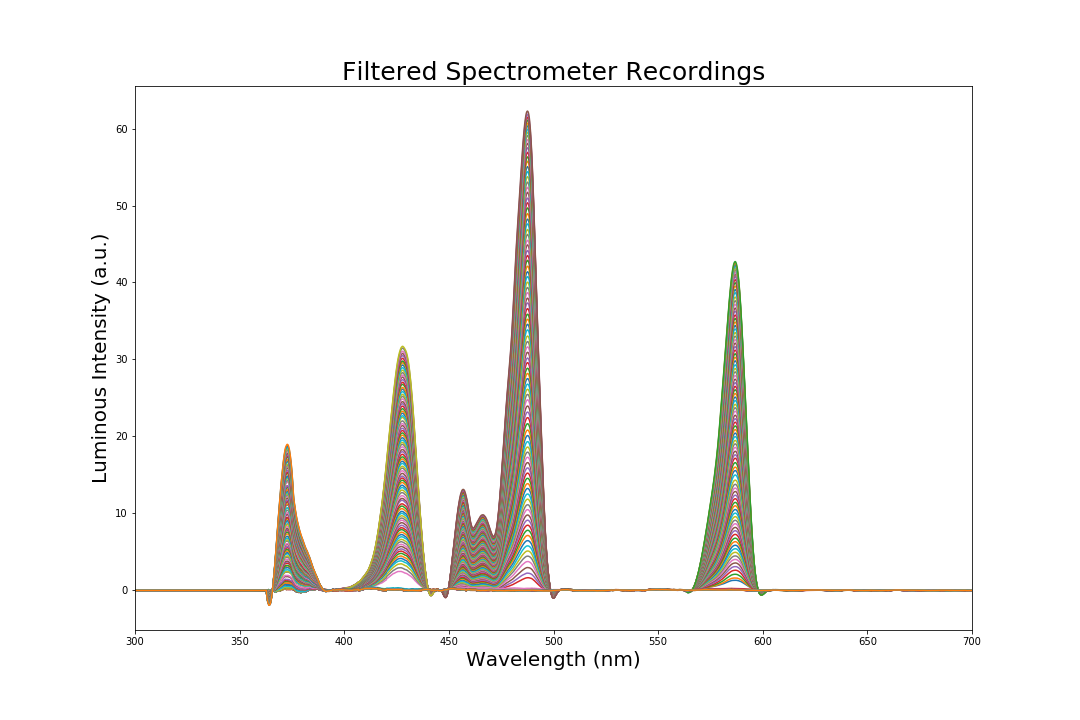
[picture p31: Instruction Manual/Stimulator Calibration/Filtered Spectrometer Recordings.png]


.

.

The script then run a couple of slides to extract and smooth (Savitzky–Golay filter) the recording data.

From this recording, the peak wavelength of each LED is extracted and assigned to the *Peaks[ ]* array.

|                     |   Red LED  |  Green LED |  Blue LED  |   UV LED   |
| --------------------|:----------:|:----------:|:----------:|:----------:|
| Peak Wavelength (nm)|    586.9   |    487.5   |    427.9   |    372.8   |

Depending on the LEDs used or on the extra resistors that a user might want to connect in series to substantially tune down the LEDs, a powermeter shall be used to bring the LEDs to their desired max values. Here we suggest to set the potentiometers at mid-range and replace the spectrometer sensor by the powermeter's. In our case, we used a [ThorLabs Digital Handheld Optical Power](https://www.thorlabs.de/newgrouppage9.cfm?objectgroup_id=3341) coupled with a [ThorLabs Photodiode Power Sensor S130VC](https://www.thorlabs.de/thorproduct.cfm?partnumber=S130VC), 200 - 1100 nm, 50 mW. Each LED is then successively brought to their desired maximum power (here 40nW) and the powermeter configured to the LED peak wavelengths (λmax). Once this value has been reached, the *max_LED* value in the LED Values part of the Arduino code has to be decreased until a change is oberved. The max_LED value is then hard-coded and fine tuning can be achieved with the potentiometers.
At this stage, one might retake measurements with the spectrometer with this new power (in our case equalised amongst LEDs), and rerun the first part of this script to obtain more precise curves.

To establish the LEDs performance we then plotted their normalised intensities (LED relative brightness) against the PWM (*array_LED#*) used in the Arduino code to drive them. A Linear fit along with the Sum of Square Error (SSE), demonstrates that the TLC5947 LED driver controls the LED in an optimal linear manner.

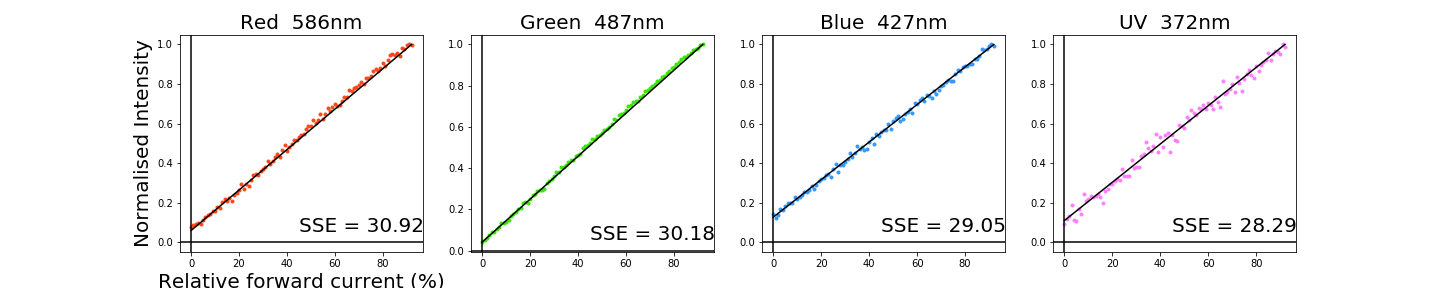
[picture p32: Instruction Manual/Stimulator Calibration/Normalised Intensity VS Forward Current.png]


***

We then used the absorbance spectrum fitting template for visual pigment defined by [Govardoskii et al, 2000 - In Search of Visual Pigment Template](https://github.com/BadenLab/Tetra-Chromatic-Stimulator/blob/master/References/Govardovskii%202000%20-%20In%20search%20of%20the%20visual%20pigment%20template.pdf). Using the Opsin maximal absorbance defined earlier, this nomogram template describes the predicted shape of the absorbance spectra of all visual pigment. Here we obtained the following specra for the zebrafish cone photoreceptors that we plotted along the human visible spectrum as comparison.

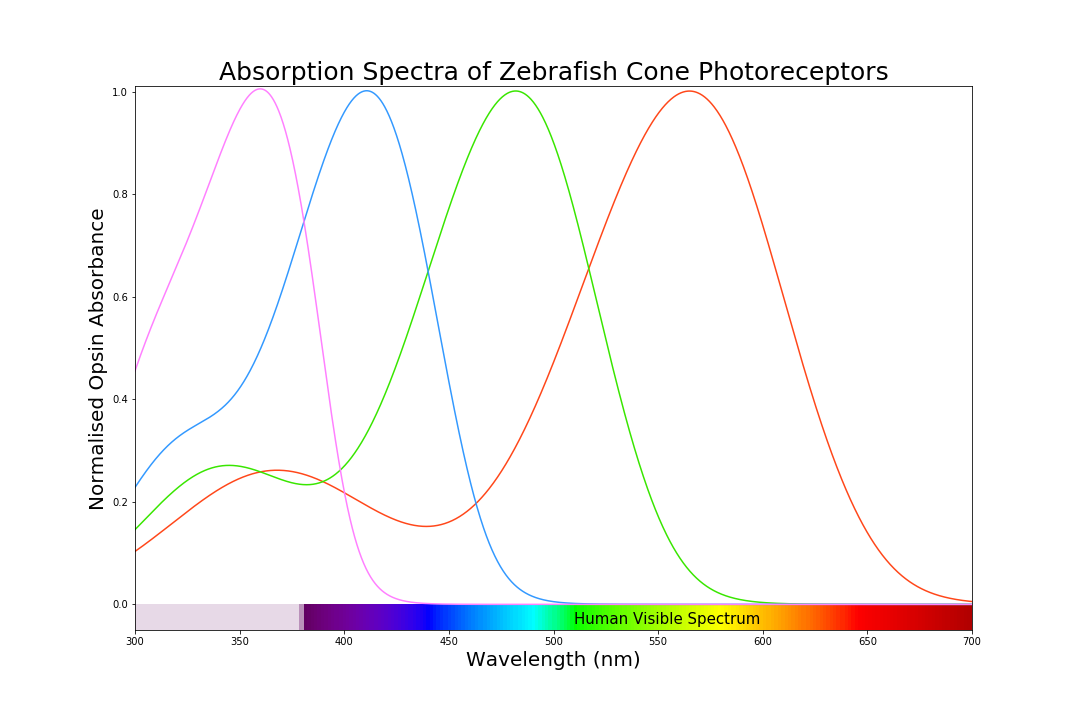
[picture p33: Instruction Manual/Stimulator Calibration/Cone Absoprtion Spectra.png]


***

Using the same display we plotted the LEDs spectra that we obtained from the spectrometer recordings.

Then, we plotted the LED spectra along the cone opsin absorbance, and each LED’s spectral cross-section with respective target conein solid colours. Grey boxes indicate the positions of the two PMT detector bands. The Red-LED’s long-wavelength emission spectrum was chosen to limit spectral overlap with the red-fluorescence detection channel. Any loss in excitation efficiency of the red opsin was compensated for by increasing this LED’s power accordingly.

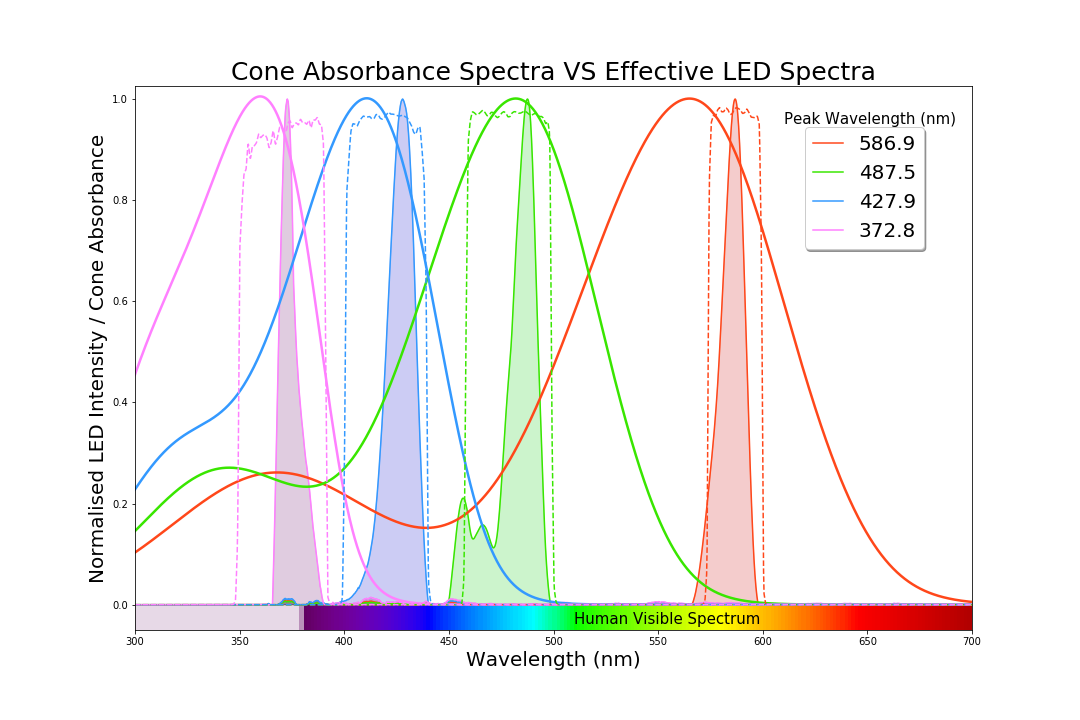
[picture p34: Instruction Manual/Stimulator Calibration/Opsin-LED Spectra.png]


***

With the previous spectra, we estimate the relative co-excitation of photoreceptors by the LEDs:
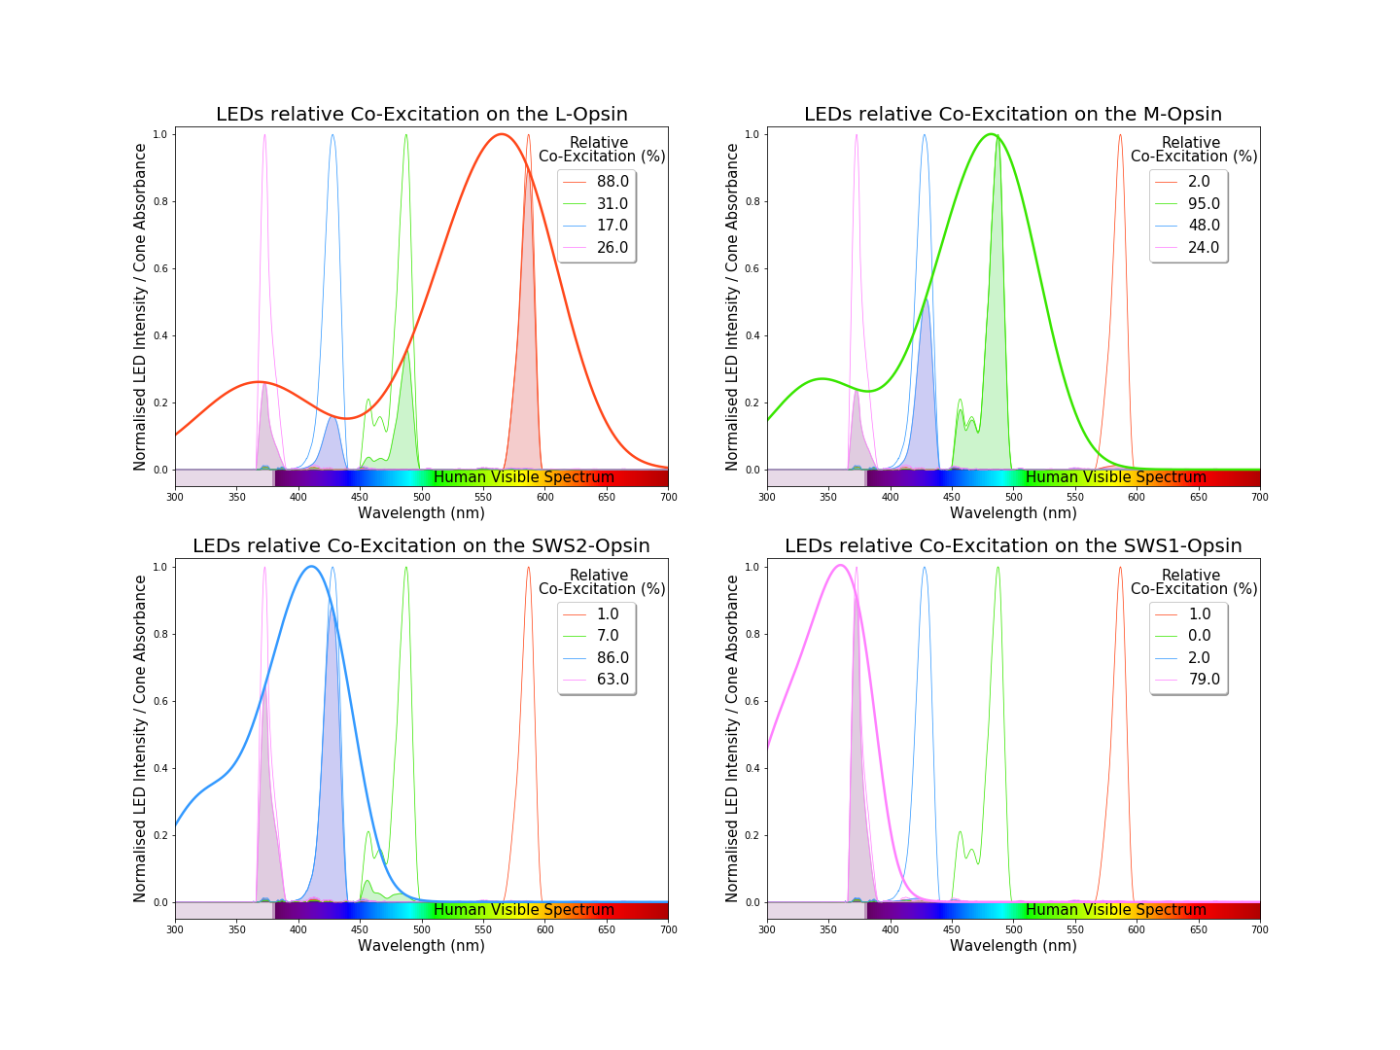
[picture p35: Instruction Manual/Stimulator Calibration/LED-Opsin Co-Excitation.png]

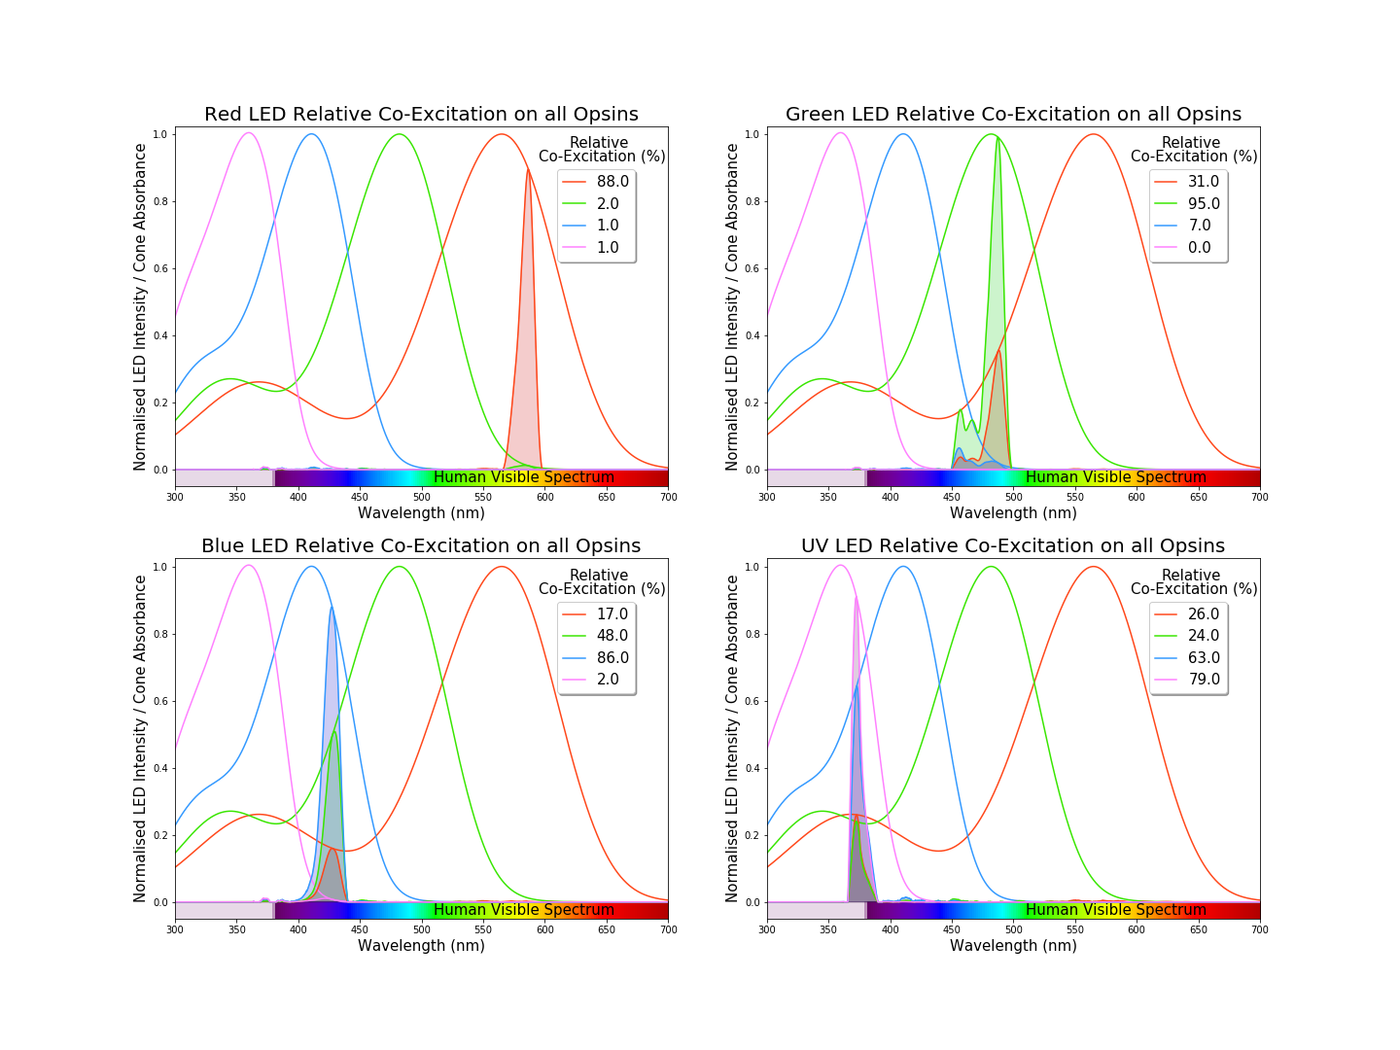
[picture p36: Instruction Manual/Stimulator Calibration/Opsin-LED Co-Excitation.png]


***

This project is licensed under the [GNU General Public License v3.0](https://github.com/MaxZimmer/Multi-Chromatic-Stimulator/blob/master/LICENSE)

***

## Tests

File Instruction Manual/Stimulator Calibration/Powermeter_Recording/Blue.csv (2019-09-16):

Optical Power Monitor
1.1.2315.102
Delimiter Used:
Start of Measurement | 8/6/2019 18:34:16
Sample Interval | 1 s
 | PM100D 18112641
Type | PM100D
Serialnumber | P0009872
Sensor | S130VC
SensorSerialnumber | 18112641
Wavelength / Responsivity | 427 nm
 |  |  | PM100D 18112641 | PM100D 18112641
Samples | Date (MM/dd/yyyy) | Time of day (hh:mm:ss) | Power (W) | Irradiance (W/cm²)
0 | 8/6/2019 | 18:34:16 | 9.8015E-11 | 1.3828E-10
1 | 8/6/2019 | 18:34:17 | -5.2799E-13 | -7.4489E-13
2 | 8/6/2019 | 18:34:18 | 4.1571E-12 | 5.8648E-12
3 | 8/6/2019 | 18:34:19 | -1.0294E-12 | -1.4523E-12
4 | 8/6/2019 | 18:34:20 | 5.1839E-11 | 7.3135E-11
5 | 8/6/2019 | 18:34:21 | -1.0566E-11 | -1.4906E-11
6 | 8/6/2019 | 18:34:22 | -1.1372E-11 | -1.6043E-11
7 | 8/6/2019 | 18:34:23 | -5.0191E-13 | -7.0809E-13
8 | 8/6/2019 | 18:34:24 | 1.1453E-12 | 1.6158E-12
9 | 8/6/2019 | 18:34:25 | 7.0013E-12 | 9.8773E-12
10 | 8/6/2019 | 18:34:26 | 2.8155E-10 | 3.9721E-10
11 | 8/6/2019 | 18:34:27 | 6.8543E-10 | 9.67E-10
12 | 8/6/2019 | 18:34:28 | 1.0813E-09 | 1.5255E-09
13 | 8/6/2019 | 18:34:29 | 1.5019E-09 | 2.1189E-09
14 | 8/6/2019 | 18:34:30 | 1.9337E-09 | 2.7281E-09
15 | 8/6/2019 | 18:34:31 | 2.3108E-09 | 3.26E-09
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

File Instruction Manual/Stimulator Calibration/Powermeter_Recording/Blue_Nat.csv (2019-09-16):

Optical Power Monitor
1.1.2315.102
Delimiter Used:
Start of Measurement | 8/6/2019 18:36:21
Sample Interval | 1 s
 | PM100D 18112641
Type | PM100D
Serialnumber | P0009872
Sensor | S130VC
SensorSerialnumber | 18112641
Wavelength / Responsivity | 427 nm
 |  |  | PM100D 18112641 | PM100D 18112641
Samples | Date (MM/dd/yyyy) | Time of day (hh:mm:ss) | Power (W) | Irradiance (W/cm²)
0 | 8/6/2019 | 18:36:21 | 5.3849E-11 | 7.597E-11
1 | 8/6/2019 | 18:36:22 | 5.6524E-11 | 7.9744E-11
2 | 8/6/2019 | 18:36:23 | 1.1686E-11 | 1.6487E-11
3 | 8/6/2019 | 18:36:24 | 2.2393E-11 | 3.1592E-11
4 | 8/6/2019 | 18:36:25 | 1.8146E-12 | 2.5601E-12
5 | 8/6/2019 | 18:36:26 | 2.2226E-11 | 3.1356E-11
6 | 8/6/2019 | 18:36:27 | 1.3192E-11 | 1.8611E-11
7 | 8/6/2019 | 18:36:28 | -1.0296E-12 | -1.4526E-12
8 | 8/6/2019 | 18:36:29 | 1.1351E-11 | 1.6014E-11
9 | 8/6/2019 | 18:36:30 | 1.9549E-11 | 2.758E-11
10 | 8/6/2019 | 18:36:31 | -1.1972E-12 | -1.689E-12
11 | 8/6/2019 | 18:36:32 | -2.5354E-12 | -3.5769E-12
12 | 8/6/2019 | 18:36:33 | 1.9814E-12 | 2.7954E-12
13 | 8/6/2019 | 18:36:34 | 8.6741E-12 | 1.2237E-11
14 | 8/6/2019 | 18:36:35 | 9.8453E-12 | 1.389E-11
15 | 8/6/2019 | 18:36:36 | 7.3589E-11 | 1.0382E-10
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

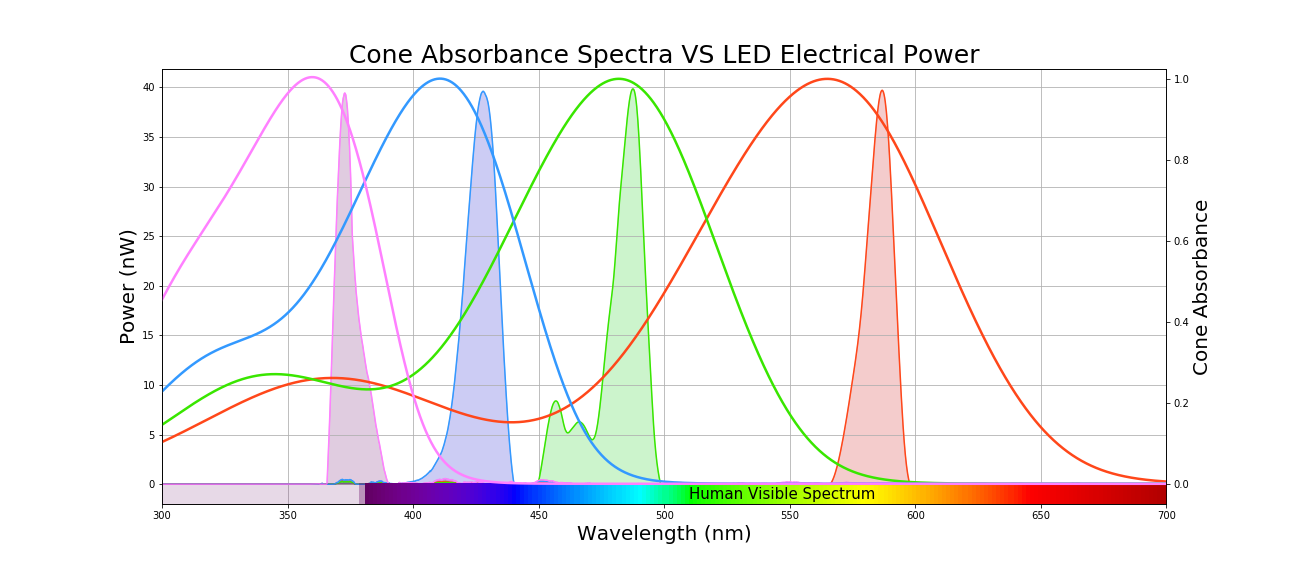
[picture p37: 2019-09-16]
Instruction Manual/Stimulator Calibration/Powermeter Recordings Sumary.png

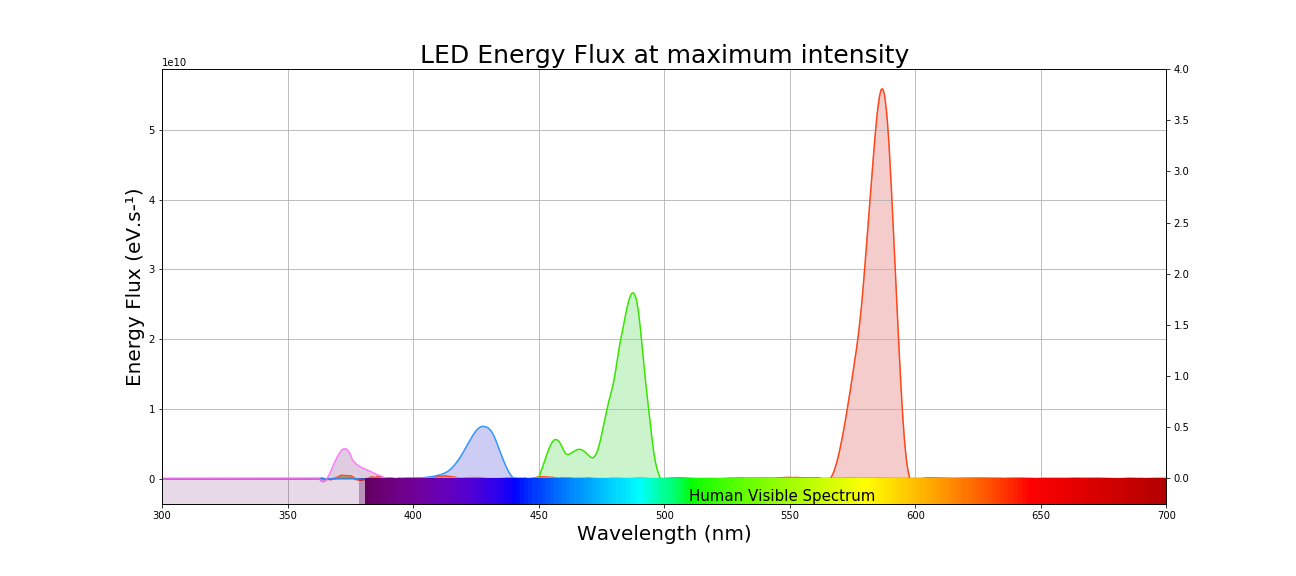
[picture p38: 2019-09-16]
Instruction Manual/Stimulator Calibration/LED Energy Flux Nat-Stat.png

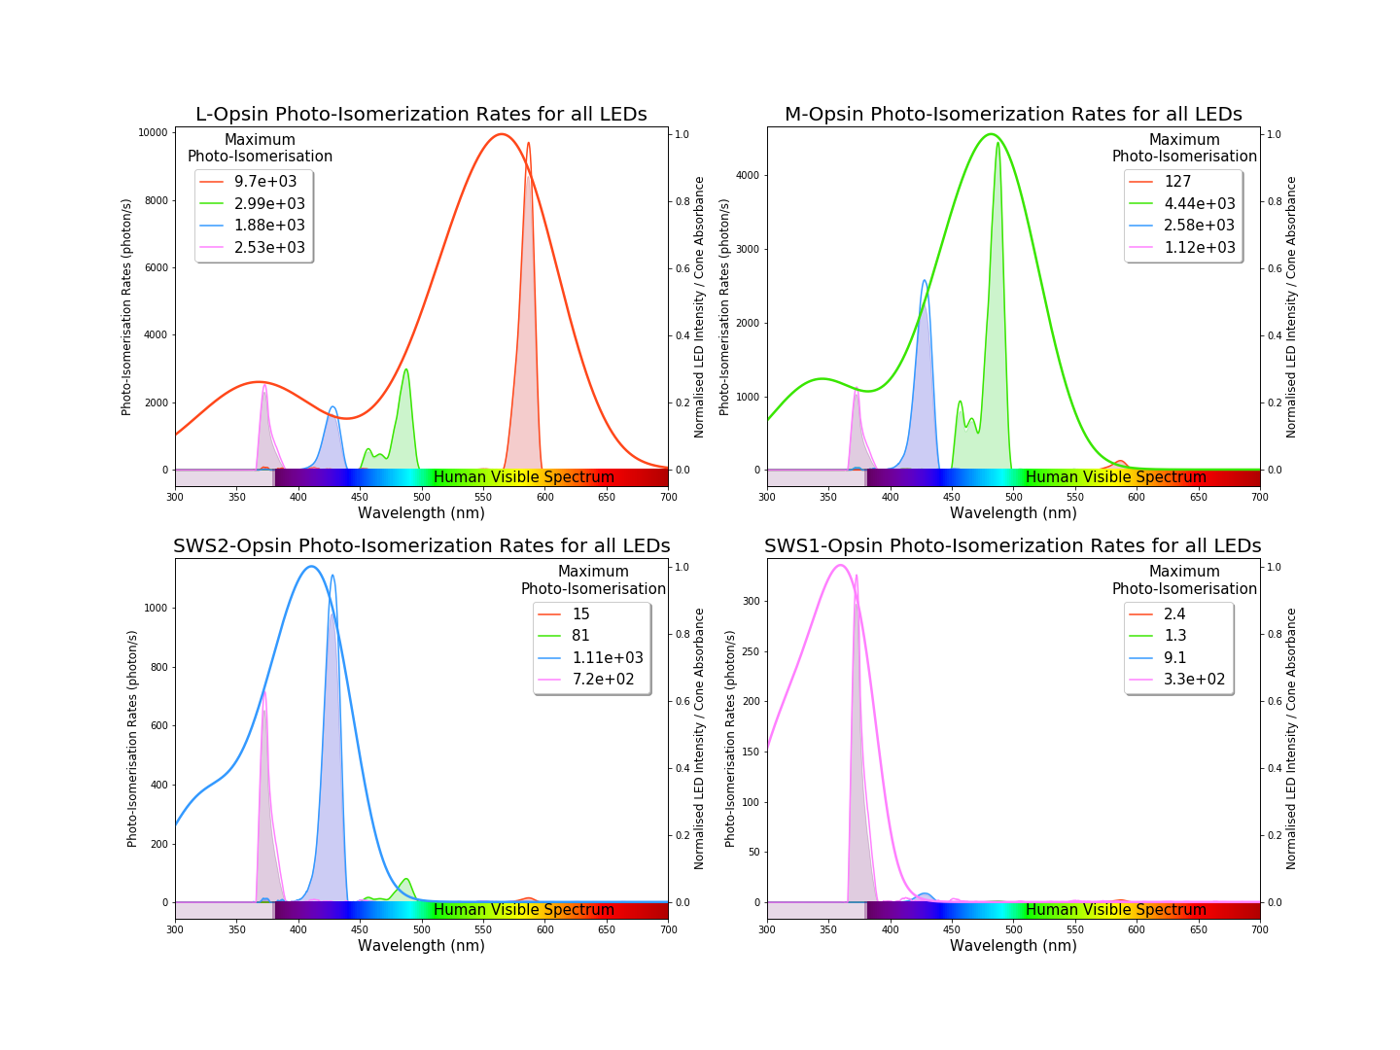
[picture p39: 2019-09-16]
Instruction Manual/Stimulator Calibration/Opsin-LED Photo-Isomerisation Rates Nat-Stat.png

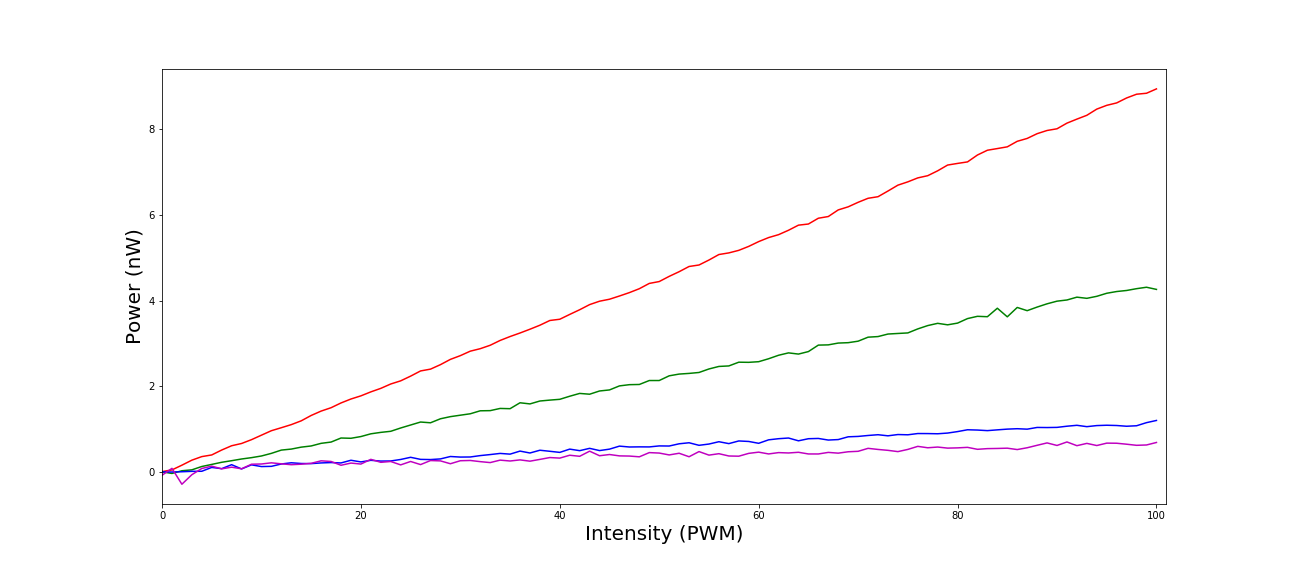
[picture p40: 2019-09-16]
Instruction Manual/Stimulator Calibration/Powermeter Recordings Nat-Stat.png

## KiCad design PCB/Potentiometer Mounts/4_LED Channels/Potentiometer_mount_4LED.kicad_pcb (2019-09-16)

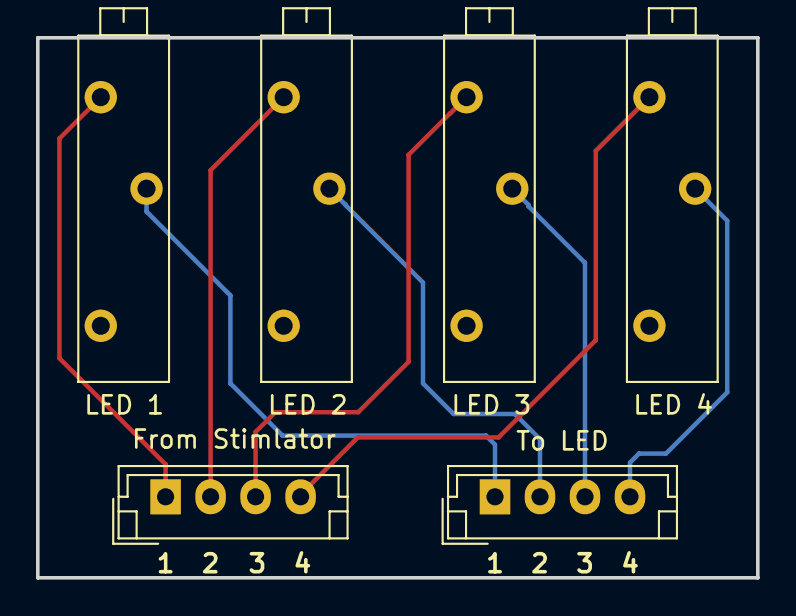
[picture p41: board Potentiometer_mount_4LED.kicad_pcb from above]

Board: 2 copper layers, 40.0 x 30.0 mm, 6 parts (0 on the bottom side), 8 nets.

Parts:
From Stimlator: JST_EH_B04B-EH-A_1x04_P2.50mm_Vertical
LED 1, LED 2, LED 3, LED 4: Potentiometer_Vishay_43_Horizontal
To LED: JST_EH_B04B-EH-A_1x04_P2.50mm_Vertical

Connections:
unnamed: From Stimlator.1, LED 1.3
unnamed: From Stimlator.2, LED 2.3
unnamed: From Stimlator.3, LED 3.3
unnamed: From Stimlator.4, LED 4.3
unnamed: LED 1.2, To LED.1
unnamed: LED 2.2, To LED.2
unnamed: LED 3.2, To LED.3
unnamed: LED 4.2, To LED.4

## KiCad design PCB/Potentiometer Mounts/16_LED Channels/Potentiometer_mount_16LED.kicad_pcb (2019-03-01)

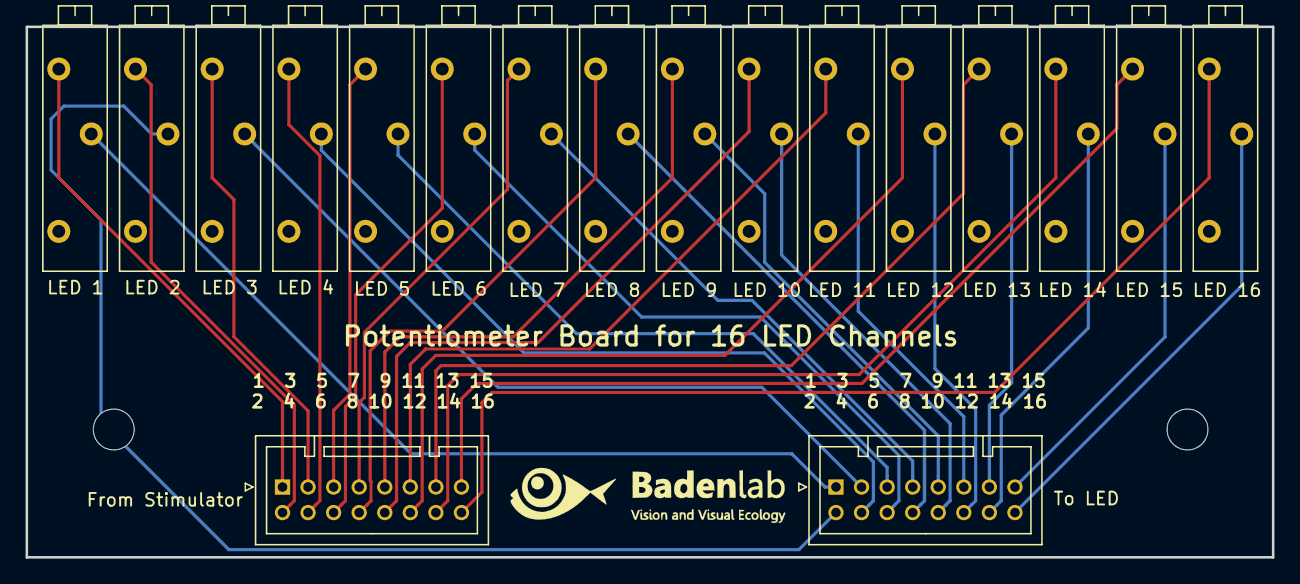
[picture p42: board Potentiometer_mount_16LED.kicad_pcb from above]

Board: 2 copper layers, 97.5 x 41.5 mm, 18 parts (0 on the bottom side), 32 nets.

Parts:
 LED 11: R_POT_TRIM; Potentiometer_Vishay_43_Horizontal
From Stimulator: JST_PUD_B16B-PUDSS_2x08_P2.00mm_Vertical
LED 1, LED 2, LED 3, LED 4: Potentiometer_Vishay_43_Horizontal
LED 5, LED 6, LED 7, LED 8, LED 9, LED 10, LED 12, LED 13, LED 14, LED 15, LED 16: R_POT_TRIM; Potentiometer_Vishay_43_Horizontal
To LED: JST_PUD_B16B-PUDSS_2x08_P2.00mm_Vertical

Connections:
unnamed: From Stimulator.1, LED 1.3
unnamed: From Stimulator.2, LED 2.3
unnamed: From Stimulator.3, LED 3.3
unnamed: From Stimulator.4, LED 4.3
unnamed: From Stimulator.5, LED 5.3
unnamed: From Stimulator.6, LED 6.3
unnamed: From Stimulator.7, LED 7.3
unnamed: From Stimulator.8, LED 8.3
unnamed: From Stimulator.9, LED 9.3
unnamed: From Stimulator.10, LED 10.3
unnamed: LED 11.3, From Stimulator.11
unnamed: From Stimulator.12, LED 12.3
unnamed: From Stimulator.13, LED 13.3
unnamed: From Stimulator.14, LED 14.3
unnamed: From Stimulator.15, LED 15.3
unnamed: From Stimulator.16, LED 16.3
unnamed: LED 1.2, To LED.1
unnamed: LED 2.2, To LED.2
unnamed: LED 3.2, To LED.3
unnamed: LED 4.2, To LED.4
unnamed: LED 5.2, To LED.5
unnamed: LED 6.2, To LED.6
unnamed: LED 7.2, To LED.7
unnamed: LED 8.2, To LED.8
unnamed: LED 9.2, To LED.9
unnamed: LED 10.2, To LED.10
unnamed: LED 11.2, To LED.11
unnamed: LED 12.2, To LED.12
unnamed: LED 13.2, To LED.13
unnamed: LED 14.2, To LED.14
unnamed: LED 15.2, To LED.15
unnamed: LED 16.2, To LED.16

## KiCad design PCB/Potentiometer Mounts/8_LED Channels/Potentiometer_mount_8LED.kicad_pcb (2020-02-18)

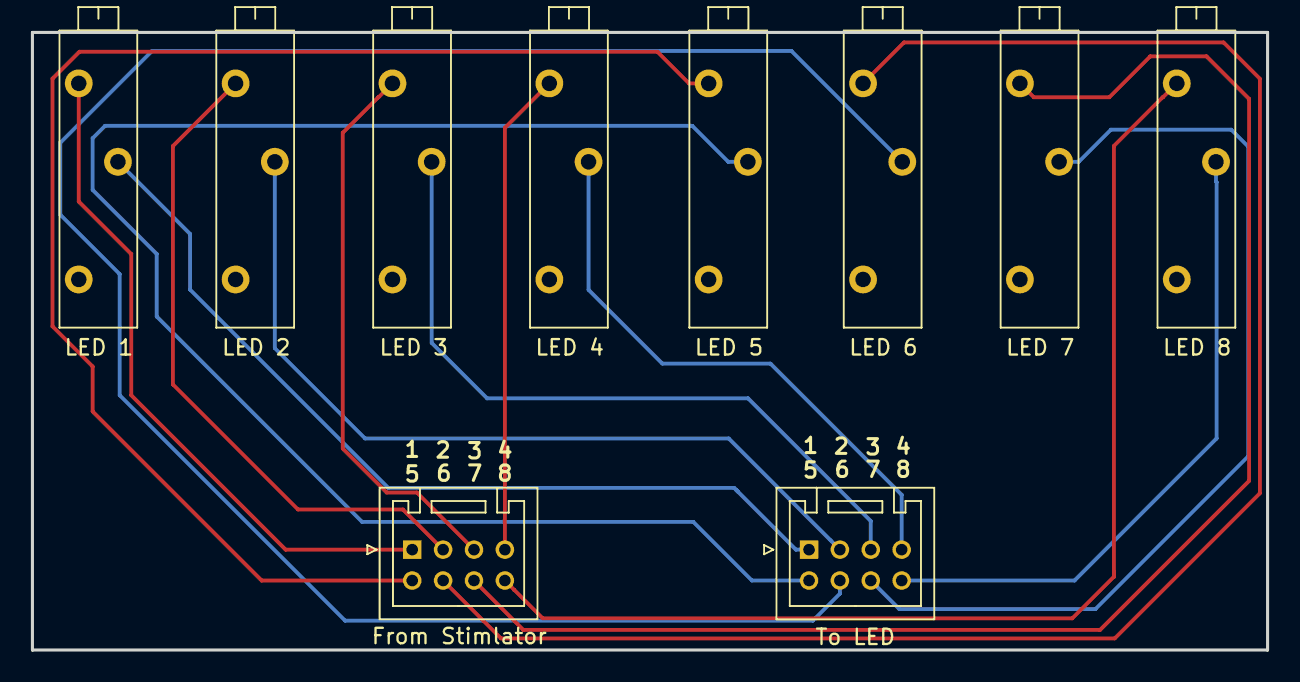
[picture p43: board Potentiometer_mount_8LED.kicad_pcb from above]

Board: 2 copper layers, 80.0 x 40.0 mm, 10 parts (0 on the bottom side), 8 nets.

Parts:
From Stimlator: JST_PUD_B08B-PUDSS_2x04_P2.00mm_Vertical
LED 1, LED 2, LED 3, LED 4, LED 5, LED 6, LED 7, LED 8: Potentiometer_Vishay_43_Horizontal
To LED: JST_PUD_B08B-PUDSS_2x04_P2.00mm_Vertical

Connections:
unnamed: From Stimlator.1, LED 1.3
unnamed: From Stimlator.3, LED 2.3
unnamed: From Stimlator.5, LED 3.3
unnamed: From Stimlator.7, LED 4.3
unnamed: LED 1.2, To LED.1
unnamed: LED 2.2, To LED.3
unnamed: LED 3.2, To LED.5
unnamed: LED 4.2, To LED.7

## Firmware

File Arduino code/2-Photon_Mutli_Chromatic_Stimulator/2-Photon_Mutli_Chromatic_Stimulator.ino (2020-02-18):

/* 
 
        The Multi Chroatic Stimulator is an open hardware LED stimulator that can individually
control up to 24 LEDs.

This Arduino file is designed to be uploaded on an Adafruit_HUZZAH ESP32 Feather or an Arduino Nano
Source : https://github.com/BadenLab/Multi_Chromatic_Stimulator

The script relies on an incoming blanking signal, generated by a TTL, which updates the LEDs.
The stimulus speed has to be adjusted to the scan logic (scanning mirrors speed that corresponds to 
the blanking signal generated by the TTL): 1kHz/1ms, 500Hz/2ms, etc.
A trigger signal is generated at the begining of the stimulus and then every 1.0 seconds.

Library "Adafruit TLC5947" needs to be installed.
 
The default script is parametered for 4 LEDs (connected to pin 0 to 3), and their respective proxy LEDs 
(connected to pin 4 to 7)


This project is Open Source licensed, released under CERN OHL v1.2

by  M.J.Y. Zimmermann, 2019.02.05
Baden Lab, CRPC, School of Life Sciences, University of Sussex, United Kingdom
*/


/* ------------------------------------------------------------------------------------
                           Stimulus parameters
-------------------------------------------------------------------------------------*/                                                                                             

int           nLoops           = 500;     //  Number of repeats of the arrays (i.e. Loops)
const int     nArrayEntries    = 3;      //  Number of entries in the arrays, including preadaption at position 0
const int     Scan_Logic      =  2;      //  Scanning logic (1 for 1ms scans, 2 for 2ms scans, etc.)



// // // // // // // // // // // // // // // // // // // // // // // // // // //
// // // // // // // // // STIMULUS SEQUENCE START // // // // // // // // // //
// // // // // // // // // // // // // // // // // // // // // // // // // // // 

// The array_LED# values are expressed in percentage and should only be expressed from 0-100
const int8_t array_LED1[] PROGMEM = {
0,100,0
};
const int8_t array_LED2[] PROGMEM = {    
0,100,0
};
const int8_t array_LED3[] PROGMEM = {    
0,100,0
};
const int8_t array_LED4[] PROGMEM = {
0,100,0
};

// The array_Time values are expressed in milliseconds
const int16_t array_Time[] PROGMEM = {      
1,2,2
};

// // // // // // // // // // // // // // // // // // // // // // // // // // //
// // // // // // //  STIMULUS SEQUENCE END  // // // // // // // // // // // //
// // // // // // // // // // // // // // // // // // // // // // // // // // //


/* ------------------------------------------------------------------------------------
                           Microcontroller Board Selection
-------------------------------------------------------------------------------------*/

      //#define Arduino_Nano
      #define Adafruit_ESP32

      
/* ------------------------------------------------------------------------------------
                    Internal Definitions (Change at your own risk)
-------------------------------------------------------------------------------------*/

#include "LED_Values.h"                     // Include LED Values defined in the second tab
#include <SPI.h>                            // Include the arduino serial port interface library
#include "Adafruit_TLC5947.h"               // Include the Adafruit TLC5947 libvrary. For better result one may change the number of channel defined in the Adafruit_TLC5947.cpp library


#ifdef Arduino_Nano
    #define   data            4             // SPI connection, DIN connected to pin D4
    #define   clock           5             // SPI connection, CLK connected to pin D5
    #define   latch           6             // SPI connection, LAT connected to pin D6
    //#define   oe              2           // Optional feature to prevent LED to light up when powering up the TLC board connected to pin D2
    const int      pSyncOut      =   A0;    // Trigger channel must be connected to pin A0
    const int      pBlank        =   3;     // Blanking signal channel must be connected to pin D3
#endif

#ifdef Adafruit_ESP32
    #define   data           18             // SPI connection, DIN connected to pin MOSI/18
    #define   clock           5             // SPI connection, CLK connected to pin SCK/5
    #define   latch          21             // SPI connection, LAT connected to pin 21
    //#define   oe            25            // Optional feature to prevent LED to light up when powering up the TLC board connected to pin A1/DAC1
    const int      pSyncOut      =   26;    // Trigger channel must be connected to pin A0/DAC2
    const int      pBlank        =   36;    // Blanking signal channel must be connected to pin A4/36
#endif

    Adafruit_TLC5947 tlc = Adafruit_TLC5947(1, clock, data, latch);

    

/* Global variables */  
char           sCmd;                        // Serial monitor 
int            i;                           // iteration loop factor
word           BaudRate      = 115200;      // Baud Rate
int            led1          = 0;           // Define 1st Channel       
int            led2          = 1;           // Define 2nd Channel
int            led3          = 2;           // Define 3rd Channel
int            led4          = 3;           // Define 4th Channel
int            proxy_led1    = 4;           // Define 1st Channel marker        
int            proxy_led2    = 5;           // Define 2nd Channel marker
int            proxy_led3    = 6;           // Define 3rd Channel marker
int            proxy_led4    = 7;           // Define 4th Channel marker
  
/* Global LED variables */
volatile word   stled1;                     // First LED value   
volatile word   stled2;                     // Second LED value
volatile word   stled3;                     // Third LED value
volatile word   stled4;                     // Fourth LED value
word            array1[nArrayEntries];      // First LED Array
word            array2[nArrayEntries];      // Second LED Array
word            array3[nArrayEntries];      // Third LED Array
word            array4[nArrayEntries];      // Fourth LED Array

/* Timing variables */
volatile word  pulse;                                             // Pulse number
word           Time[nArrayEntries];                               // Time Array
float          x_Logic            =   1.0/Scan_Logic;             // Factor applied to the timing according to the scanning logic

/* Trigger variables */
int     Trigger_Duration            =   25;                       // Length of the Trigger signal in ms
int     TriggerCounter_Duration     =   1000;                     // Lenght of the Trigger loop in ms
word    Trigger_dur        =   Trigger_Duration * x_Logic;        // Trigger signal duration adjusted
word    TriggerCounter_dur =   TriggerCounter_Duration * x_Logic; // Trigger loop duration adjusted  
    
/* Reset Parameters */
volatile word  iLoop                = 0;       // Actual loop number = iLoop + 1
volatile word  PulseCount           = 0;       // Count the number of pulses delivered by the blanking signal
volatile int   PulseCount_Trigger   = 0;       // Count the number of pulses generated for the trigger channel (A0 pin)
volatile int   ArrayPosition        = 0;       // Position array within the current loop

/* Flags */
bool   SettingFlag   =  true;
bool   BlankingFlag  =  true;


/* -----------------------------------------------------------------------------------
                                 Internal methods
 ------------------------------------------------------------------------------------*/

void setup(){

// Initialise the serial communication with PC
  Serial.begin(BaudRate);

// Initialise the Adafruit TLC driver 
  tlc.begin();
  tlc.write();  

// Set pins
  pinMode(pSyncOut, OUTPUT);  
  digitalWrite(pSyncOut, LOW);  
  pinMode(pBlank, INPUT);
  digitalWrite(pBlank, HIGH);
}

/* ----------------------------------------------------------------------------------*/
/* -------------------------------- Turn all LED off --------------------------------*/

void Play0(){
      tlc.setPWM(led1,0);                                // Set First LED to 0
      tlc.setPWM(led2,0);                                // Set Second LED to 0
      tlc.setPWM(led3,0);                                // Set Third LED to 0 
      tlc.setPWM(led4,0);                                // Set Fourth LED to 0
      tlc.setPWM(proxy_led1,0);                          // Set First proxy LED to 0
      tlc.setPWM(proxy_led2,0);                          // Set Second proxy LED to 0
      tlc.setPWM(proxy_led3,0);                          // Set Third proxy LED to 0 
      tlc.setPWM(proxy_led4,0);                          // Set Fourth proxy LED to 0
      tlc.write();   
      Serial.println("-> All LEDs off"); 
      
      PulseCount = 0;                                    // Reset Pulse counter
      PulseCount_Trigger = 0;                            // Reset Trigger pulse counter
      ArrayPosition = 0;                                 // Reset Array counter
      
      SettingFlag = true;                                // Return to initial condition
      BlankingFlag = true;                               // Return to initial condition
}



/* ----------------------------------------------------------------------------------*/
/* ------------------------------ Play Stimulus Array -------------------------------*/

void PlayArrays() {

/* Defining timing according to the current array position */
    pulse = Time[ArrayPosition];
    
/* Trigger ------------------------------------------------------------------------*/

    /* Keep Trigger on for the trigger duration */
    if(PulseCount_Trigger <= Trigger_dur && ArrayPosition > 0){
        PulseCount_Trigger += 1;                         // Trigger Pulse Counter, move to the next pulse
    } 
    /* Keep Trigger off for the rest of the trigger duration */
    if(PulseCount_Trigger > Trigger_dur && ArrayPosition > 0){
        digitalWrite(pSyncOut, LOW);                     // Turn Trigger off
        PulseCount_Trigger += 1;                         // Trigger Pulse Counter, move to the next pulse
    }

    /* Once Trigger duration is reached, reset counter and turn trigger on */
    if(PulseCount_Trigger == TriggerCounter_dur+1 && ArrayPosition > 0){
        PulseCount_Trigger = 0;                          // Reset Trigger pulse counter
        digitalWrite(pSyncOut, HIGH);                    // Turn Trigger on
    }
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

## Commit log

2019-02-25 Update Optical Components.scad
    [Optical Components.scad]
2019-03-12 3D files for LED Holder
    [LED_holder.scad, LED_holder.stl]
2019-03-14 Update Datasheet
    [ACA254-050-A-AutoCADDXF.dxf, ACA254-050-A-Solidworks.sldprt, ACA254-050-A-Step.step]
2019-03-14 Update BoM
    [BOM - Optics.csv]
2019-03-22 3D Design update
    [1 LED Holder.stl, Back.stl, Bottom.stl, Front.stl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]
2019-03-22 Update BOM - Optics.csv
    [BOM - Optics.csv]
2019-04-23 Spectrum Calibration update
2019-04-25 25/04/2019 update
    [Ops1.csv, Ops2.csv, Ops3.csv, Ops4.csv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]
2019-04-25 Calibration Script Update
    [Ops1.csv, Ops2.csv, Ops3.csv, Ops4.csv]
2019-06-13 2019.06.16 update
    [Badenlab_logo.stl, Blue.csv, Green.csv, Left.stl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]
2019-07-31 Version 2.1 update
    [Blue.csv, Green.csv, Multi Chromatic Stimulator-B.Cu.gbr, Multi Chromatic Stimulator-B.Mask.gbr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]
2019-09-16 Create Circuit Drawing.png
2019-09-16 Update Supplementary Material.odt
